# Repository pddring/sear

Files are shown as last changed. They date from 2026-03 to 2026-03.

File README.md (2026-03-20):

# sear


Sear is our entry to the PA Consulting Raspberry Pi Competition 2026 from Fulford School KS3.

## About Sear
Our project is called SEAR (Seeing ear) and it focuses mainly on the Healthier Humans part of this year’s theme of the PA Consulting competition.

Many people in society can’t see, and although most can get treatment or help easily, not everyone can get treatment as they might not have access to it or might not be able to afford it. This means that they are left out of education, employment and entertainment.

A little while back, a visually impaired student joined our school. We wanted to help her as she faced a multitude of difficulties ranging from not being able to participate in physical lessons like drama and PE to not understanding what was going on.  Not being able to see what was on the board made it hard for her as she had to work harder to understand what was going on. 

She has a teaching assistant who was her eyes for her as the assistant told her what was going on in the lesson. This was great but this meant that she was dependent on the assistant and we wanted to help become independent.

So, we started working on a device to better her school and overall life.
That is where SEAR comes in. It is a cost effective and efficient AI powered speaking camera which uses a Raspberry Pi to take a picture of what it sees and then describes it to the user.

It is unique in many ways. For example, it is suitable for school as in our school phones are banned: making it is a better alternative to a phone, where you will get in trouble for using it.

Everyone in our team is autistic so we know what it feels like to be excluded and we didn't want anyone else to feel this way, so we started working on a device to help them.

We created SEAR to help visually impaired students thrive in all aspects of life.
It helps them be:
**Safer**: They can know about their surroundings and can keep themselves safe.
**Happier**: They can join in with activities they wouldn't be able to participate in normally.
**Healthier**: They won’t need to be cautious and scared anymore.

# Build instructions: hardware

Use the Raspberry Pi installer to install a Raspberry Pi OS Lite (64 bit) image to a micro SD card for your raspberry pi (tested on a Raspberry Pi 3B v1.2 but we used a Raspberry Pi Zero 2 W)

You will need to connect some push switches to 4 GPIO pins:

- Middle button (white) to BCM pin 2
- Right button (green) to BCM pin 3
- Left button (blue) to BCM pin 4
- Top button (red) to BCM pin 22

We soldered these on a prototyping board with headers so it would plug in on top of the raspberry pi zero:
{C74A0183-AE29-4668-9B7F-E0921284E3B7}

{A6F4F192-AF0A-46CB-A0C6-BDD28C138EDD}

We designed the casing in Fusion and printed it on a Creality K1C using PLA in two parts: 

Top: 
{46EBAE07-D8B7-4F37-BD93-4DD2711C0A69}

Bottom:
{4A3DCC7C-A16C-482D-9F5B-EC7D22D911FC}

We used a USB recharable battery pack and a camera which fits into the case as shown below:
{42C25944-D81C-42B9-BE46-63027A7721F2}

## Setup instructions
You will need a Google Gemini API key for this to work.
You can create one here: https://aistudio.google.com/app/api-keys

Clone this repository to get a copy of the source code on the raspberry pi:
`git clone https://github.dev/pddring/sear`

Create a `settings.json` file in the src folder:
```
{
    "API_KEY":"INSERT YOUR API KEY HERE",
    "camera_id": 0
}
```
Install the following system libraries
`sudo apt install libportaudio-ocaml-dev bluez-alsa-utils pulseaudio pulseaudio-module-bluetooth`

Add the user to the bluetooth group:
`sudo adduser pi bluetooth`

Create a virtual environment:
`virtualenv --system-site-packages venv`

Activate that virtual environment:
`source venv/bin/activate`

install additional libraries:
`pip install gpiozero google-genai opencv-python pyaudio azure-cognitiveservices-speech azure-ai-vision-imageanalysis`

# Usage instructions
We added a script to make the code run automatically on start up, but if you want to make it run manually, you can do this by enabling the virtual environment (as shown above) then running:
`python main.py`

When the progrma runs you can attempt to connect to the closest bluetooth speaker / headset by placing the sear device next to the speakers and holding down the top button

Pressing the top button rather than holding it should give a status update (speaking the time and speaker battery life)

Pressing the middle button should take a picture and describe what it sees, speaking the description through bluetooth speakers.

# Future plans
We haven't yet made it so that the sear device can measure how much battery charge is left. It can read the battery life of the bluetooth speaker but there's no way to detect when the main battery runs down. We've ordered a sensor which we could directly connect to the battery inside the battery pack but we haven't connected that up yet.

We haven't yet coded it to fast forward / repeat the last speech using the left and right button. We hope to get that working soon

Attempting to connect to the closest bluetooth headset or speaker doesn't always work reliably and sometimes you need to do this in the terminal using `bluetoothctl` then `scan on` to show all devices. This should show the MAC addresses of all detected devices, then you can do `connect 00:00:00:00:00` (replacing the MAC address with the one for the device you want to connect to.

# List of parts
| Part | Link | Price |
| --- | --- | --- |
| Raspberry Pi Zero 2 W | https://shop.pimoroni.com/products/raspberry-pi-zero-2-w?variant=42101934587987 | £14.40 |
| Raspberry Pi Camera | https://shop.pimoroni.com/products/raspberry-pi-camera-module-v2?variant=19833929735 | £14.40 |
| Battery pack | We used a free promotional one a bit like this: https://www.highflyers.de/p/span-1200-mah-powerbank-2513427700-p.html | £3.00 |
| Bluetooth speaker | Any bluetooth headset would work | Not included in price |
| | Totals: | £31.80 |

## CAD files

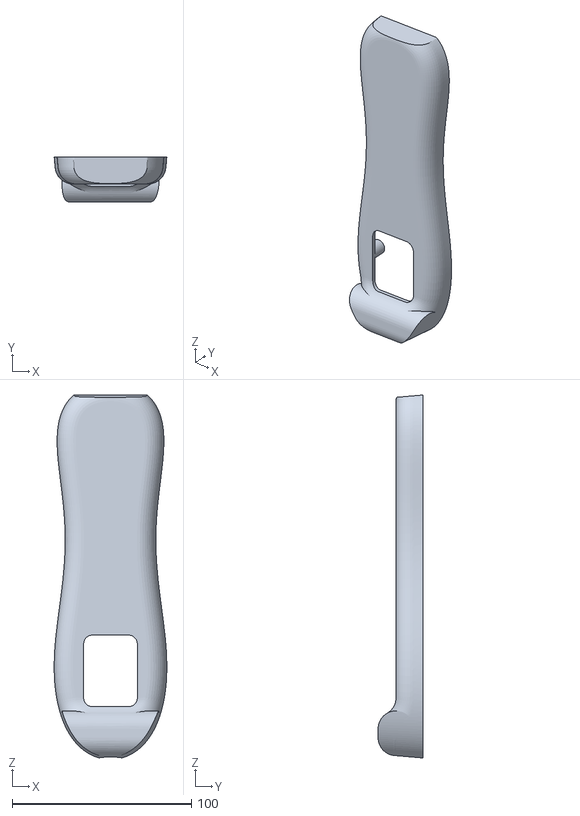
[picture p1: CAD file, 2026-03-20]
3d models/Sear case top.stl
62.9 x 25.0 x 202.6

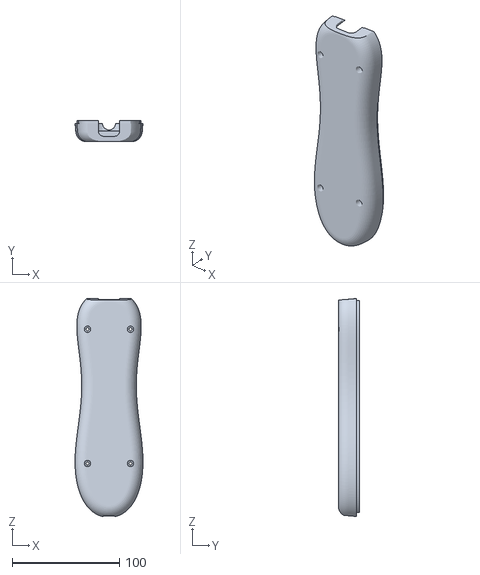
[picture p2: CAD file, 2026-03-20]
3d models/Sear case bottom.stl
63.3 x 20.0 x 203.0

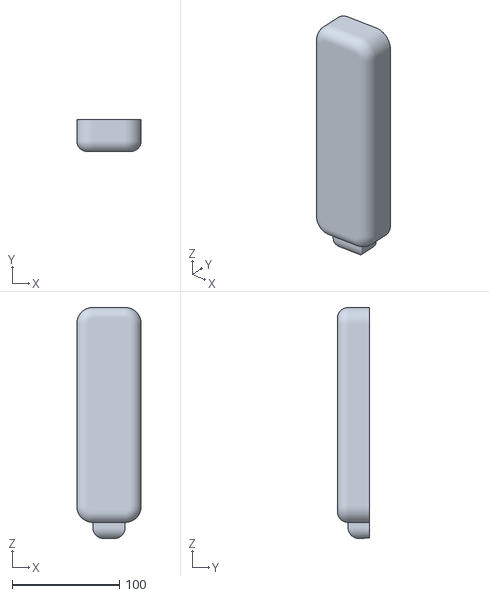
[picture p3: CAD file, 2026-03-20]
3d models/Sear case.stl
60.0 x 30.0 x 215.0

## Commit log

2025-10-12 Working prototype
2025-10-16 Enhance README with setup instructions for Raspberry Pi
    Updated setup instructions for Raspberry Pi and Google Gemini API.
2025-10-17 print output devices
2025-10-17 added support to choose output device
2025-10-17 fixed output device list
2025-10-17 Auto selects bluetooth devices
2025-10-17 added warm up code to camera
2026-02-28 Long press red to connect to bluetooth device
    Doesn't yet scan for closest device - has to have been added manually
2026-03-20 Added 3d models
    [Sear case bottom.stl, Sear case top.stl, Sear case.stl]
